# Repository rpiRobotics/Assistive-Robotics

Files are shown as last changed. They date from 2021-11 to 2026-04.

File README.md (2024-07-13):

# Assistive Robotics

This is a repository for multi-robot assitive applications that utilizes Clearpath Dingo Omni-directional robots.

# Computers in the System:

| Description                     | Username      | Hostname (Computer Name) | MAC Address       | IP            | Password  | OS           | ROS     |
| ------------------------------- | ------------- | ------------------------ | ----------------- | ------------- | --------- | ------------ | ------- |
| GUI Tablet                      | tablet        | tablet20                 | AC:67:5D:57:30:50 | 192.168.1.99  | 1234      | Ubuntu 20.04 | Noetic  |
| Main Computer                   | ???           | ?????                    | 3C:8C:F8:EB:0E:C8 | 192.168.1.100 | ????      | Ubuntu 20.04 | Noetic  |
| Dingo 1 Base (Right Arm Config) | administrator | cpr-do100-10000050       | 0C:7A:15:CB:A6:0B | 192.168.1.101 | clearpath | Ubuntu 20.04 | Noetic  |
| Dingo 1 Helper                  | oarbot_blue   | oarbot-blue-P15          | F4:46:37:FF:E5:A1 | 192.168.1.102 | 1234      | Ubuntu 18.04 | Melodic |
| Dingo 2 Base (Left Arm Config)  | administrator | cpr-do100-10000051       | F0:B6:1E:B7:29:1F | 192.168.1.103 | clearpath | Ubuntu 20.04 | Noetic  |
| Dingo 2 Helper                  | oarbot_silver | oarbot-silver-P15        | 4C:77:CB:EC:81:87 | 192.168.1.104 | 1234      | Ubuntu 18.04 | Melodic |
| Overhead Camera Kinect Processor| nuc           | nuc-18                   | 1C:69:7A:0D:A3:E0 | 192.168.1.90  | 1234      | Ubuntu 18.04 | Melodic |

# Setting up the system

<details> 
    <summary>Click to expand</summary>

<!-- Simply run
```
./all_devices_initial_setup.bash
``` -->

</details>

<!-- --------------------------------------------------------------------------- -->

# Setting up the Helper Computers

<details> 
    <summary>Installing Ubuntu 18.04 to Lenovo Thinkpad P15 Gen2 Laptops</summary>

## Installing Ubuntu 18.04 to Lenovo Thinkpad P15 Gen2 Laptops

See the hardware specs of this computer model in https://psref.lenovo.com/syspool/Sys/PDF/ThinkPad/ThinkPad_P15_Gen_2/ThinkPad_P15_Gen_2_Spec.pdf

We have
CPU: Core i7-11850H
GPU: NVIDIA T1200 (4GB GDDR4, 60W)
RAM: 16 GB DDR4-3200MHz
SCREEN: 1080P IPS
STORAGE: 512GB SSD M.2 2280 SSD PCIe NVMe
WIFI: Intel Wi-Fi® 6E AX210, 802.11ax 2x2 Wi-Fi + Bluetooth 5.2

### Prepare the BIOS settings

As described here: https://download.lenovo.com/pccbbs/mobiles_pdf/tp_p1_gen2_ubuntu_18.04_lts_installation_v1.0.pdf
(Note that this file is for P1, not for P15, so not all of steps here works for installing ubuntu 18.04 to P15)

- Disable "OS Optimized Defaults" in "Restart"
- Make sure "Hybrid Graphics" is selected instead of "Discrete Graphics" under Config>Display settings. Later we will have to make this "Discrete Graphics" again.
- F10 "Save & Exit"

### Install Ubuntu 18.04 with a USB

- Insert Ubuntu 18.04 installation USB and boot up the laptop.
- Press "Enter" while you are booting.
- Press "F12" to select the USB device.
- In the GRUB menu select "Install Ubuntu"
- Make sure you are connected to internet via Ethernet (WIFI does not work for now)
- Select Normal installation,
- For the Other options select "Download Updates while installing Ubuntu" and "Install third-party software for graphics and Wifi hardware..." options
- Do the storage managements as you wish (I did without encryption)
- For the username and computer name use the devices info table at the top of this readme file.
- After the installation if the computer does not boot after the GRUB menu, (see https://askubuntu.com/questions/162075/my-computer-boots-to-a-black-screen-what-options-do-i-have-to-fix-it.)
- Basically you will boot with nomodeset option  in the grub menu instead of quiet splash and then you will install graphics card after you boot in
- While booting keep pressing "shift" buttons to see GRUB menu,
- Press "e" while the OS that you would like to boot is selected.
- Go to line that starts with "linux" and erase "quiet splash" and write "nomodeset" instead.
- Press "Ctrl+x", you will be able to boot
- We will have to install NVIDIA graphics card and WIFI drivers

### Install NVIDIA drivers

- open a terminal and do `sudo apt update` and `sudo apt upgrade`
- press windows key and search for "Software & Updates"
- From ubuntu Software tab select Download From Main Server
- From Updates tab Select Never for Notify me of a new Ubuntu version
- From Additional Drivers tab select Using Nvidia driver metapackage from nvidia-driver495 (proprietary)
- Press Apply Changes button and once it finished reboot
- This will install the NVIDIA driver but you can also see options of the section 5 of [this](https://download.lenovo.com/pccbbs/mobiles_pdf/tp_p1_gen2_ubuntu_18.04_lts_installation_v1.0.pdf) for other installation options (We did not try those)
- When it boots up, go to BIOS settings and select "Discrete Graphics" instead of "Hybrid Graphics" under Config>Display settings.
- Save and Exit
- Once you reboot, now without doing the "nomodeset" step in GRUB menu you will be able to login

### Install Wifi Drivers

At the time of this installation, the most up-to-date Ubuntu 18.04 kernel version is 5.4.0 (you can check yours with command `uname -a`). However, the wifi hardware used on this computer (Intel Wi-Fi® 6E AX210) requires at least kernel version 5.10 (You can verify this at [here](https://wireless.wiki.kernel.org/en/users/drivers/iwlwifi)).
As stated in one of the answers in [this link](https://ubuntu.forumming.com/question/14149/ubuntu-20-04-lts-driver-intel-wi-fi-6e-ax210-160mhz), "The Linux 5.10 kernel (or later) will ship as part of Ubuntu 21.04 in April. This version will also get backported to Ubuntu 20.04 LTS at a later date. It's possible to manually install a mainline kernel in Ubuntu however if it breaks you get the pieces." We will install kernel 5.11 to make the wifi adapter work, but as suggested in the same answer be warned to review the implications of installing a kernel version manually [here](https://askubuntu.com/questions/119080/how-to-update-kernel-to-the-latest-mainline-version-without-any-distro-upgrade/885165#885165).

#### Installing Kernel 5.11

- First install Mainline as a graphical kernel installing tool. (See details [here](https://ubuntuhandbook.org/index.php/2020/08/mainline-install-latest-kernel-ubuntu-linux-mint/))
- run `sudo add-apt-repository ppa:cappelikan/ppa`
- `sudo apt update`
- `sudo apt install mainline`
- Open Mainline Kernel Installer and install 5.11.0
- After installation, reboot.
- `sudo update-grub` and `sudo reboot`
- As described [here](https://github.com/spxak1/weywot/blob/main/ax210.md#boot-with-kernel-5101), the output of `sudo dmesg | grep iwl` will show us some errors with the information about which firmware we need to install.
- For example we needed `iwlwifi-ty-a0-gf-a0-39` to `iwlwifi-ty-a0-gf-a0-59`.

#### Installing Firmware

- At the output of dmesg command it is suggested to check https://git.kernel.org/pub/scm/linux/kernel/git/firmware/linux-firmware.git/
- Go this website and download the newest firmware (eg. as of today it was linux-firmware-20211027.tar.gz (sig))
- It takes some time to download, be patient
- Uncompress the file with `tar -zxvf linux-firmware-20211027.tar.gz`
- `cd linux-firmware-20211027/`
- Copy the firmwares to `/lib/firmware/` with command `sudo cp -ax * /lib/firmware`
- Now reboot and the wifi should work!

### Additional settings

- Connect the wifi to lab network.
- Open settings on Privacy tab, disable automatic screen lock, location services enabled.
- Sharing tab, enable sharing and screen sharing, select require a password and make the password `1234`
- Power tab, disable dim screen when inactive, blank screen 5 minutes, Automatic suspend OFF, When power button is pressed Power Off
- Details tab, Users tab, Unlock and enable automatic log in
- Install GNOME Tweaks and launch
- On Power tab disable suspend when laptop lid is closed
- Install Dconf Editor and launch
- on /org/gnome/desktop/remote-access, disable require-encryption
- `sudo apt install ssh`

### Install ROS Melodic

- See [here](http://wiki.ros.org/Installation/Ubuntu)

</details>

<details> 
    <summary>Setting Up Kinect Azure</summary>

## Setting Up Kinect Azure

Setup the Sensor SDK and Body SDK for Kinect Azure following https://docs.microsoft.com/en-us/azure/kinect-dk/sensor-sdk-download and https://docs.microsoft.com/en-us/azure/kinect-dk/body-sdk-download .

At the time of this document the support is only for Ubuntu 18.04 with an AMD64 architecture CPU, additionally a dedicated GPU is a must (with minimum model specified as NVIDIA Geforce GTX 1050 see [here](https://docs.microsoft.com/en-us/azure/kinect-dk/system-requirements) for other requirements)

The steps are summarized as:

### Ssh into the Kinect Processor Computer of the robots

The passwords are given at the top for the  Kinect Processors. Use the information given and ssh into the robots. For example,

```
ssh oarbot_blue@192.168.1.101
```

or

```
ssh oarbot_silver@192.168.1.102
```

Then on each robot, follow the steps below:

### Setting up Linux Software Repository for Microsoft Products

```
curl -sSL https://packages.microsoft.com/keys/microsoft.asc | sudo apt-key add -
sudo apt-add-repository https://packages.microsoft.com/ubuntu/18.04/prod
sudo apt-get update
```

### Setting up the SDKs

```
sudo apt install libk4a1.4-dev
sudo apt install libk4abt1.1-dev
sudo apt install k4a-tools
```

### Adding permissions for Azure Kinect as a usb device

```
cd /etc/udev/rules.d
sudo wget https://github.com/microsoft/Azure-Kinect-Sensor-SDK/blob/develop/scripts/99-k4a.rules
```

Plug in the USB of Kinect Azure and connect it to the power. Then you can verify the installation with `k4aviewer` or `k4abt_simple_3d_viewer` commands.

### Setting up the ROS packages for Kinect Azure

(See the instructions for building [here](https://github.com/microsoft/Azure_Kinect_ROS_Driver/blob/melodic/docs/building.md) as reference)

```
sudo apt-get install ros-melodic-rgbd-launch
cd ~/catkin_ws_assistive/src
git clone https://github.com/burakaksoy/Azure_Kinect_ROS_Driver.git
cd ..
catkin_make -DCATKIN_WHITELIST_PACKAGES='azure_kinect_ros_driver'
source ~/.bashrc
source ~/catkin_ws_assistive/devel/setup.bash
```

#### Troubleshooting:
    
If you see this kind of error during the `catkin_make` command execution:

```
    Finding K4A SDK binaries
    CMake Error at Azure_Kinect_ROS_Driver/cmake/Findk4a.cmake:22 (message):
    Error: Azure Kinect SDK Version numbers contain exactly 3 components
    (major.minor.rev).  Requested number of components: 2
    Call Stack (most recent call first):
    /usr/local/share/cmake-3.18/Modules/CMakeFindDependencyMacro.cmake:47 (find_package)
    /usr/lib/cmake/k4abt/k4abtConfig.cmake:3 (find_dependency)
    Azure_Kinect_ROS_Driver/cmake/Findk4abt.cmake:35 (find_package)
    Azure_Kinect_ROS_Driver/CMakeLists.txt:94 (find_package)

    -- Configuring incomplete, errors occurred!
```

Change 2 components in the version number given in this line of file `/usr/lib/cmake/k4abt/k4abtConfig.cmake` from this:

```
find_dependency(k4a 1.3 REQUIRED)
```

to this:
```
find_dependency(k4a 1.3.0 REQUIRED)
```
and try again the `catkin_make` command above. 

*For more information about this issue see: [https://github.com/microsoft/Azure_Kinect_ROS_Driver/issues/143](https://github.com/microsoft/Azure_Kinect_ROS_Driver/issues/143)*

### Adjusting Default launch parameters for Azure Kinect

You can edit the default FPS argument value to 30 in `/src/Azure_Kinect_ROS_Driver/launch/kinect_rgbd.launch`.

Finally you can verify Kinect Ros installation working by

```
roslaunch azure_kinect_ros_driver kinect_rgbd.launch
```

and in a new terminal you can check for the published images with

```
rqt_image_view
```

For further information about the topics and the usage see https://github.com/microsoft/Azure_Kinect_ROS_Driver/blob/melodic/docs/usage.md

### Bonus: Installing Kinect Azure on Ubuntu 20.04
(Source: https://github.com/microsoft/Azure-Kinect-Sensor-SDK/issues/1263#issuecomment-1705808614)

```
sudo apt purge libk4a*
sudo apt purge k4a
sudo apt purge k4a*
sudo apt autoremove 
sudo apt remove libk4a*
sudo apt remove libk4abt*
sudo apt remove libk4a1*
curl -sSL https://packages.microsoft.com/keys/microsoft.asc | sudo tee /etc/apt/trusted.gpg.d/microsoft.asc
sudo apt-add-repository https://packages.microsoft.com/ubuntu/20.04/prod
sudo apt-get update
curl -sSL https://packages.microsoft.com/keys/microsoft.asc | sudo tee /etc/apt/trusted.gpg.d/microsoft.asc
sudo apt-add-repository https://packages.microsoft.com/ubuntu/20.04/prod
curl -sSL https://packages.microsoft.com/keys/microsoft.asc | sudo apt-key add -
sudo apt-add-repository https://packages.microsoft.com/ubuntu/18.04/prod
curl -sSL https://packages.microsoft.com/config/ubuntu/18.04/prod.list | sudo tee /etc/apt/sources.list.d/microsoft-prod.list
curl -sSL https://packages.microsoft.com/keys/microsoft.asc | sudo apt-key add -
sudo apt-get update
sudo apt install libk4a1.4=1.4.1
sudo apt install libk4a1.4-dev=1.4.1
sudo apt install libk4abt1.1-dev=1.1.2
sudo apt install k4a-tools=1.4.1
sudo apt install ros-noetic-rgbd-launch

# Copy rules
# sudo cp 99-k4a.rules /etc/udev/rules.d/

# k4aviewer
# k4abt_simple_3d_viewer 
```

Also hold these packages to prevent update:
```
sudo apt-mark hold libk4a1.4
sudo apt-mark hold libk4a1.4-dev
sudo apt-mark hold libk4abt1.1-dev
sudo apt-mark hold k4a-tools
# sudo apt-mark showhold
# sudo apt-mark unhold <package-name>
```

Moreover, in the `cmakelists.txt` file of the kinect ros package you may need to edit:
```
# find_package(k4a 1.4.0 QUIET MODULE REQUIRED)
find_package(k4a 1.3.0 QUIET MODULE REQUIRED)

...

# find_package(k4abt 1.1.0 QUIET MODULE)
find_package(k4abt 1.0.0 QUIET MODULE)
```

### Bonus 2: How to resolve high CPU usage issue with body tracking
(Source: https://github.com/microsoft/Azure-Kinect-Sensor-SDK/issues/1007)
Set openMP environment variable as 
`export OMP_WAIT_POLICY=Passive`
before launching kinect!!!

</details>

<details> 
    <summary>Setting Up Kinova Arm for robots</summary>

## Setting Up Kinova Arm for robots

### Hardware Setup

1. Plugin the powercable and the joystick
2. Connect the USB cable to your laptop
3. Powerup the arm

The green light on the joystick will be flashing for around a minute. After that, there will be two results after you do that

#### Joystick Steady Green light

You are good to go! Please direct to [software setup](#software-setup).

#### Joystick Green Light flashing or Steady Red Light

You need to update the firmware of the arm. If you try to use the ROS package when this situation happens, it'll show connection error.

1. Please follow the instruction in this [webpage](https://github.com/Kinovarobotics/kinova-ros/issues/248).
2. You can find the latest firmware [here](https://www.kinovarobotics.com/en/resources/gen2-technical-resources).
3. You can find the installation files of Development Center, a GUI available with the SDK [here](https://www.kinovarobotics.com/en/resources/gen2-faq) in the first question of "Usage". If the download link is missing, you can find it [here](https://drive.google.com/file/d/1UEQAow0XLcVcPCeQfHK9ERBihOCclkJ9/view) (File name is "`PS 0000 0009_1.5.1.zip`") and the document [here](https://www.kinovarobotics.com/sites/default/files/UG-008_KINOVA_Software_development_kit-User_guide_EN_R02%20%281%29.pdf) or [here](https://drive.google.com/file/d/1y5TByFsF97s4_zh14E-q0YHSlMr5P1qe/view).
4. We only tested the Development Center in win10 while updating the firmware. However, Development Center in both win10 and ubuntu20.04 (using the ubuntu16.04 version in the file) can connected to the arm and control the arm.
5. While rebooting the arm in the updating firmware step, you might want to do some "physical therapy" for the arm (basically move the arms around) and wait a bit before restarting your arm.

### Software Setup

#### Control the arm via Development Center

You can find the installation files of Development Center, a GUI available with the SDK [here](https://www.kinovarobotics.com/en/resources/gen2-faq) in the first question of "Usage". If the download link is missing, you can find it [here](https://drive.google.com/file/d/1UEQAow0XLcVcPCeQfHK9ERBihOCclkJ9/view) and the document [here](https://www.kinovarobotics.com/sites/default/files/UG-008_KINOVA_Software_development_kit-User_guide_EN_R02%20%281%29.pdf).

#### Add Translation offset if you have Bota Rokubi FT sensors installed on Kinova robots

Since the Kinematics change due to the additional hardware with the installed FT sensor, we need to add translation offset to the robot settings. 

- Open up the Development Center from `/opt/JACO-SDK/GUI/DevelopmentCenter`. 
- From `General Settings` enter `0.077` to `z-axis` (the other axes are 0).
- Select the check box that says `Activate Offset`.
- Hit `Save` button.

Note that after reboot of the arm the check box is automatically unchecked. Instead of opening the Development Center each time, on the joystick of the arm one can press 1 button. It lits up the right most blue light on the joystick which indicates the offset is activated. 

#### Control the arm via ROS package

Please direct [here](https://github.com/eric565648/kinova-ros/tree/noetic-devel) for how to launch the arm, perform joint angle and cartetian space control.

#### Put the arm to service mode

- Plug in USB your robot
- Open the `C:\Program Files (x86)\JACO-SDK\RobotConfiguration` or the equivalent path on you system.
- Put the last firmware you upload in your robot in the firmware folder.
- Run `ActivateServiceConfiguration.exe` (it is a console app, see the outputs by running it from a terminal/command line)
  If that works well at  General setting > update at the arm type field you will see JAco v2 6dof Service.

#### To use admittance control

1. Open Development Center GUI, general setting > update
2. Verify that main firmware is updated.
3. Arm type is in service mode (see above).
4. Actuator firmware is updated.
5. Verify that all the torque sensors are functional. (see details below)
6. Do the torque calibration. (see details below)
7. Verify that the gravity vector and the payload correctly defined. (see details below)

##### Steps 1-4 are already done in the above.

##### 5. Verifying all torque sensors are functional

Open the Development Center and go to Monitoring >angular >torque  column

- Push against each joint to apply an external torque to each joint and observe if the value on screen reacts
  accordingly to your action. Push in both direction and the torque should be positive in one direction and
  negative in the opposite one.
- If it does not react as expected, You have a problem with one or more of your torque sensor.
- If it reacts as expected, try step 6.

##### 6. Doing the torque calibration

Calibrate arm torque by reset sensors to zero value.
Get the user Guide. Go at the page 58 and place the robot at the picture position (candle like position)

- Once the arm is in the right position, you have to open the Development Center and go to Advanced settings and press 4 times to the Apply to all button in torque zero menu.
- Try to put the arm in torque mode with torque console, but close the Development Center before opening Torque console.
- If the arm does not switch to torque control try step 7.

##### 7. Verify that the gravity vector and the payload correctly defined.

- Open the Torque Console Interface and set the Gravity vector.
- Then set the payload if you have one.
- When it is done, try to switch to torque mode with the Torque Console Interface

If after all of those step it continue to not work, it may be a hardware issue. That need further investigation

</details>

</details>

<!-- --------------------------------------------------------------------------- -->

# Setting Up Dingo Base Computers

<details> 
    <summary>Getting Started</summary>

## Getting Started

Four Dingo-O robots arrived with a printed document named "Custom Robot Quickstart Guide". We only needed to apply section 3 and section 5 of this document after the batteries are fully charged (both the robot batteries and the PlayStation controller batteries). The texts are in these sections are copied below:

### Section 3: Getting Started

Your system has been configured to allow you to get started immediately after receipt. Follow these instructions to get
moving.

1. Remove the Dingo's side panels and top fairings (yellow), insert the batteries provided (or confirm they are
   inserted), then replace the top fairings and side panels.
2. Turn on the Dingo via the HMI button pad on the rear. Note that the computer may beep when starting up.
3. Press "PS" button on gamepad to turn it on.

### Section 5: Wireless

To set up the wireless communications on your Dingo, you must either first establish a wired Ethernet connection or use the HDMI output and USB keyboard from the robots's computer. If you use the Ethernet option, connect your computer to an Ethernet port on the Dingo's computer by removing the Dingo fairing, and set a
static IP on your computer to `192.168.131.19` (for example). If there are no free ethernet ports you may temporarily disconnect
one of the payloads such as a lidar sensor. SSH into the robot computer with:

```
ssh administrator@192.168.131.1
```

Enter the login password when prompted. Once you have successfully logged in, you can connect the robot's computer to a desired wireless network.

If you use the HDMI and USB keyboard option, when you bootup the robot, the login terminal screen of Ubuntu comes up. Enter in the username and password given at the top of this document and log in.

Once you log in, you can connect your robot to a desired wireless network using Netplan.

Simply create a file called `60-wireless.yaml` inside of the `/etc/netplan folder` on your robot's computer. Copy and paste
the contents below into the file, and make sure to modify the wireless interface, SSID, and password fields.

```txt
network:
    wifis:
    # Replace WIRELESS_INTERFACE with the name of the wireless network device, e.g. wlane or wlp3s0
    # Fill in the SSID_GOES_HERE and PASSWORD_GOES_HERE fields as appropriate. The password may be included
    as plain-text
    # or as a password hash. To generate the hashed password, run
    # echo -n 'WIFI_PASSWORD' | iconv -t UTF-16LE | openssl md4 -binary | xxd -p
    # If you have multiple wireless cards you may include a block for each device.
    # For more options, see https://netplan.io/reference/
    WIRELESS_INTERFACE:
        optional: true
        access-points:
            SSID_GOES HERE:
            password: PASSWORD_GOES_HERE
        dhcp4: true
        dhcp4-overrides:
            send-hostname: true
```

Once you have saved the file, you will then need to apply your new Netplan configuration and bring up your wireless
connection by running:

```bash
sudo netplan apply
```

More advanced networking examples, including configurations for accessing a wifi network requiring WPA Enterprise
credentials, can be found here:
https://netplan.io/examples/

You can verify that your robot is connected to a wireless network by running:

```bash
ip a
```

This will show all active connections and their IP addresses, including your robot's connection to the desired wireless
network, and the IP address assigned to the robot's computer.

</details>

<details> 
    <summary>Disable the WiFi Power Saving</summary>

List the wifi devices with command:
```
iw dev
```

To check the current power management setting of your WiFi interface, use the following command (Assuming the device is `wlp2s0`):
```
iw dev wlp2s0 get power_save
```

To Disable Power Saving Temporarily (Assuming the device is `wlp2s0`):
```
sudo iw dev wlp2s0 set power_save off
```

To Make the disabling permenant, create a Systemd Service:
```
sudo nano /etc/systemd/system/wifi-power-management.service
```

Paste the following:
```
[Unit]
Description=Disable WiFi Power Management
After=network.target

[Service]
Type=oneshot
ExecStart=/sbin/iw dev wlp2s0 set power_save off
RemainAfterExit=yes

[Install]
WantedBy=multi-user.target
```

Make sure to replace `wlp2s0` with the actual name of your wireless interface.

To enable and start the service:
```
sudo systemctl enable wifi-power-management.service
sudo systemctl start wifi-power-management.service
```

To verify (Assuming the device is `wlp2s0`):
```
iw dev wlp2s0 get power_save
```

**Note:** I also tried installing `NetworkManager` and edit its config file `sudo nano /etc/NetworkManager/conf.d/default-wifi-powersave-on.conf` by making 
```
[connection]
wifi.powersave = 2
```
and then `sudo systemctl restart NetworkManager`. 
However this did not disable the WiFi power management when I tried to verify with `iw dev wlp2s0 get power_save` command. Therefore I selected to use creating Systemd Service. 

</details>

<details> 
    <summary>Needed Software Customizations on a factory fresh Dingo-O robot</summary>

## Needed Software Customizations on a factory fresh Dingo-O robot

**WARNING: You may want to create a backup of the edited files before begin the process described here.**
To make the dingo robots work as desired in this repository, there are some customizations needed.

Follow the instructions in `ReadMe.md` file of in `src/dingo_customization/` of this repository.

</details>

<details> 
    <summary>Physical UWB setup</summary>

## Physical UWB setup

### Related websites for the Qorvo (DecaWave) UWB module documents

DW1000 [https://www.qorvo.com/products/p/DW1000#documents](https://www.qorvo.com/products/p/DW1000#documents)

DW1001C [https://www.qorvo.com/products/p/DWM1001C#documents](https://www.qorvo.com/products/p/DWM1001C#documents)

DWM1001-DEV [https://www.qorvo.com/products/p/DWM1001-DEV#documents](https://www.qorvo.com/products/p/DWM1001-DEV#documents)

MDEK1001 [https://www.qorvo.com/products/p/MDEK1001#documents](https://www.qorvo.com/products/p/MDEK1001#documents)

### Download the Android DRTLS phone app

[https://www.qorvo.com/products/p/MDEK1001#documents](https://www.qorvo.com/products/p/MDEK1001#documents)

Download DRTLS App : Android Application APK

### Calibration Script

Used to determine the every module's (tags and anchors) offsets based on [this white paper with name: Antenna Delay Calibration of DW1000-Based Products and Systems (Application Note APS014)](https://www.qorvo.com/products/d/da008449).

Set 4 of them an on a nice square with best possible known manual position measurements.

(3 of them gives only one solution, 4 of them gives a Least Squares solution with RMSE error to have an idea of how accurate the calculated offsets are.)

Take note of the manually measured distances, they are needed in the calibration script.

From the android app, put all the modules in the same network and set them as anchors. From the powered ones, only one of them must be set as initiator.

Use `antenna_offset_finding.m` MATLAB script in `uwb_matlab_scripts/` directory of this repo to find the offsets of each UWB module. Then set the offsets in `antenna_calibration.yaml` in `src/assistive_launch/config/` folder. Comments of the script should be sufficient to guide you for further details.

Note: This script would work on Windows 10 but not in Windows 11 as of writing this document. See details [here](https://www.mathworks.com/matlabcentral/answers/1912280-bluetooth-scanning-error-in-windows-11-solutions#answer_1173820)

This script uses the BLE interface of the firmware to communicate with the tags. For further information see section 7 of [DWM1001 Firmware API Guide](https://www.qorvo.com/products/d/da007975)

After the calibration is done, set modules back as tags those you won't to use as anchors from the Android app.

### Script to Calculate and Write the Anchor positions into the Modules

Mount the UWB anchors in the physical workspace area. Measure the distances between them with a laser distance meter.
Use `truck_bay_uwb_locations.m`  MATLAB script in `uwb_matlab_scripts/` directory of this repo. Comments of the script should be sufficient to guide you for further details.

Note: This script would work on Windows 10 but not in Windows 11 as of writing this document. See details [here](https://www.mathworks.com/matlabcentral/answers/1912280-bluetooth-scanning-error-in-windows-11-solutions#answer_1173820)

This script uses the BLE interface of the firmware to communicate with the tags. For further information see section 7 of [DWM1001 Firmware API Guide](https://www.qorvo.com/products/d/da007975)

### Configuring USB Ports of the UWB Tags Mounted on the Robots

At each robot equipped with the UWB tags, this step is required to read data from the UWB tags. 

Determine the USB serial ports of the UWB tags by unplugging and re-pluggin the USB cables of the tags and using this command:

```
ls /dev/serial/by-path/
```

The determined port should be something like this:

```
/dev/serial/by-path/pci-0000:00:14.0-usb-0:3:1.0
```

For each UWB tag, edit the `<robot_name>_uwb_<# of the UWB tag>.yaml` config files in `assistive_launch/config/` directory and assign the `serial_port` parameter to the determined port. 

For example, we name the first Dingo robot as `d1` and the USB port of its `2`nd UWB tag is specified in `assistive_launch/config/d1_uwb_2.yaml` file with the following content:

```
serial_port: '/dev/serial/by-path/pci-0000:00:14.0-usb-0:3:1.0'
topic_name: 'uwb/tag_2_serial_ranging'
```

</details>

<!-- --------------------------------------------------------------------------- -->

# Setting Up Tablet (Graphical User Interface Device) Computer

The tablet device as the GUI of the system is based on 'ARM Smart Teacpendant Project' hardware.

<details> 
    <summary>Tablet OS Setup</summary>

## Tablet OS Setup

### Steps to install Ubuntu (20.04 or 18.04) on Surface Go 2 Tablet

Requires a USB-C to USB-A adapter and flash drive

1. Update Windows 10/11 using Settings -> Updates
2. Download and create Ubuntu 20.04 amd64 USB install drive
3. Disable Windows bitlocker and reboot. If it says “waiting to active”, finish activation, then disable: https://www.isunshare.com/windows-10/4-ways-to-remove-or-disable-bitlocker-encryption-on-windows-10.html
4. Shrink the Windows 10 partition using Windows disk manager: https://www.tenforums.com/tutorials/96288-shrink-volume-partition-windows-10-a.html Suggested to shrink by 64000 MB
5. Connect bootable USB drive and reboot using advanced startup options: https://www.digitalcitizen.life/boot-your-windows-10-pc-usb-flash-drive The bootable usb drive may have the title “Linpus Lite”
6. Install Ubuntu as normal
7. Remove the USB drive
8. At this point Ubuntu is installed, but will not boot automatically. Do the advanced startup options again, and select “ubuntu”. This will boot into Ubuntu.
   Follow these instructions in Ubuntu to disable Windows boot: https://www.reddit.com/r/SurfaceLinux/comments/egds33/possible_fix_for_booting_directly_to_grub_on/ Windows can still be booted using Grub menu
   Ubuntu should now boot. The post is copied here for convenience:

   ```
       Possible fix for booting directly to grub on Surface Go
       If you're having trouble getting your Surface Go to boot to grub instead of the Windows Boot Manager, I might have something to try if you're brave: I moved the Microsoft folder in /boot/efi/EFI out of the way (In Ubuntu: sudo mv /boot/efi/EFI/Microsoft /boot/efi/EFI/Microsoft.bak) and now grub is loaded by default. I'd really only recommend this if you:

       Have a Windows USB recovery made and you know it's bootable

       Have your files backed up off the SSD (both Linux and Windows (if you care))

       Feel comfortable screwing around fixing a potentially broken EFI partition

       Aren't the sort of person who blames other people when you break your own computer following instructions you found on the Internet!

       All that said, it works for me on my recently purchased 8GB/128GB Surface Go w/ Ubuntu 19.10. I had already dumped the WIndows partition though, so I never tested whether grub had any issues loading Windows. You may also need to mess around with efibootmgr to fix the boot order, but I'm not sure.
   ```
9. You may also need to disable secure boot. This is achived from the BIOS settings. To enter the BIOS settings, while powering up the tablet, Press and hold the volume-up button on your Surface and at the same time, press and release the power button. When you see the Surface logo, release the volume-up button.
   The UEFI menu will display within a few seconds.
10. The default kernel version installed with ubuntu 20.04 as of writing this document is 5.15 however this version causes hanging problem when shutting down. Installing kernel version 5.4.243 via Mainline kernel installer resolves the issue for this specific tablet.
11. After the install of the OS, make sure the wifi power saving is disabled by editing:

    ```bash
    sudo nano /etc/NetworkManager/conf.d/default-wifi-powersave-on.conf
    ```

    By default there is:

    ```txt
    [connection]
    wifi.powersave = 3
    ```

    **Change the value to 2**. Then to take effect, run:

    ```bash
    sudo systemctl restart NetworkManager
    ```

    Disabling wifi power saving reduces the wifi latency by a considerable amount! For more information see [here](https://gist.github.com/jcberthon/ea8cfe278998968ba7c5a95344bc8b55).

    ### For further reducing latency, you can tune the network stack with the following commands:

    ```
    sudo sysctl -a | grep ipv4
    sudo sysctl -w net.ipv6.conf.all.disable_ipv6=1
    sudo sysctl -w net.ipv6.conf.default.disable_ipv6=1
    sudo sysctl -w net.ipv6.conf.lo.disable_ipv6=1
    sudo sysctl -w net.core.rmem_default=10000000
    sudo sysctl -w net.core.wmem_default=10000000
    sudo sysctl -w net.core.rmem_max=16777216
    sudo sysctl -w net.core.wmem_max=16777216
    sudo sysctl -w net.ipv4.tcp_low_latency=1  # intended to give preference to low latency over higher throughput; setting =1  # disables IPV4 tcp prequeue processing
    sudo sysctl -w net.ipv4.tcp_timestamps=0  # Only advised in cases where sack is needed.
    sudo sysctl -w net.ipv4.tcp_sack=0  # setting to 1 enables selective acknowledgment for IPV4, which requires enabling tcp_timestamps and adds some packet overhead, which you don't need if you don't experience packetloss
    sudo sysctl -w net.ipv4.tcp_window_scaling=1  # RFC 1323 - support for IPV4 TCP window sizes larger than 64K - generally needed on high bandwidth networks
    sudo sysctl -w net.ipv4.tcp_reordering=3  # The maximum times an IPV4 packet can be reordered in a TCP packet stream without TCP assuming packet loss and going into slow start.
    sudo sysctl -w net.ipv4.tcp_fastopen=1  # Enable to send data in the opening SYN packet.

    sudo sysctl -p # to apply the changes without rebooting

    sudo systemctl restart NetworkManager
    ```

    Note that these changes are not persistent and will be lost after a reboot. To make them persistent, you can add them to the `/etc/sysctl.conf` file as follows:

    ```
    sudo nano /etc/sysctl.conf
    ```

    Paste the following:
    ```
    net.ipv6.conf.all.disable_ipv6 = 1
    net.ipv6.conf.default.disable_ipv6 = 1
    net.ipv6.conf.lo.disable_ipv6 = 1
    net.core.rmem_default = 10000000
    net.core.wmem_default = 10000000
    net.core.rmem_max = 16777216
    net.core.wmem_max = 16777216
    net.ipv4.tcp_low_latency = 1  # intended to give preference to low latency over higher throughput; setting =1  # disables IPV4 tcp prequeue processing
    net.ipv4.tcp_timestamps = 0  # Only advised in cases where sack is needed.
    net.ipv4.tcp_sack = 0  # setting to 1 enables selective acknowledgment for IPV4, which requires enabling tcp_timestamps and adds some packet overhead, which you don't need if you don't experience packetloss
    net.ipv4.tcp_window_scaling = 1  # RFC 1323 - support for IPV4 TCP window sizes larger than 64K - generally needed on high bandwidth networks
    net.ipv4.tcp_reordering = 3  # The maximum times an IPV4 packet can be reordered in a TCP packet stream without TCP assuming packet loss and going into slow start.
    net.ipv4.tcp_fastopen = 1  # Enable to send data in the opening SYN packet.
    ```

    After adding the changes to the `/etc/sysctl.conf` file, you can apply them by running the following command:

    ```
    sudo sysctl -p # to apply the changes without rebooting

    sudo systemctl restart NetworkManager
    ```

    or you can reboot the machine to apply the changes.

    For more information on tuning the network stack, you can refer to the following resources:
    - [https://serverfault.com/q/623780/1102034] (https://serverfault.com/q/623780/1102034)
    - [https://www.speedguide.net/articles/linux-tweaking-121] (https://www.speedguide.net/articles/linux-tweaking-121)
    - [https://itsfoss.com/speed-up-slow-wifi-connection-ubuntu/] (https://itsfoss.com/speed-up-slow-wifi-connection-ubuntu/)

</details>

<!-- --------------------------------------------------------------------------- -->

# System Bootup Process Instructions

<details> 
    <summary>Click to expand</summary>

***Warning:** The order in the following instructions are important for successful bootup process. Following the order especially in the Dingo battery powered up components (Dingo base computer, Dingo helper computer, and Kinova arm) is essential, because otherwise Dingo robots may shut down after ~30 seconds, probably as a default protective measurement by Clearpath (Further investigation is needed on this matter).*

1. Make sure that on each Dingo robot, the Kinova arm is switched off, the Dingo helper computer charger is unplugged, and the robot batteries are connected and charged. 
2. Turn on the master/main computer and run `roscore`.
3. Turn on the GUI tablet.
4. Make sure the overhead Kinect camera is plugged in to the power and connected to the Kinect Azure computer. 
5. Turn on the Overhead Camera (Kinect Azure) computer (NUC).
6. Turn on each Dingo robot by using the button on the robot rear. 
7. Wait for the robot computer to complete its boot up process. 

    *This will launch the default robot control nodes, IMU node, UWB localization nodes, and front and rear Lidar sensor nodes*
8. Switch on the Kinova arm on the robots.
9. Plug in the Dingo helper computer charger.
10. Turn on the Dingo helper computer.  
11. Wait for the Dingo helper computer complete its boot up process. 
12. On master computer, launch `` file. 

     *This launch file will remotely launch
    the GUI node on the GUI tablet,
    the overhead camera and ArUco tag detection robot localization related nodes on the Overhead Camera computer (NUC),
    the Kinova arm, FT Sensor, and Kinect cameras on the Kinova arm wrist on each Dingo helper computer.
    Also, in the master/main computer it will launch
    the human body localization fusion.*

    Note that further devices, nodes, and features can be added to each computer without updating the information written in the last explanation above. That paragraph is intended to cover the main idea of system architecture which explains what system component runs on which computer in the system and therefore to create a sense on the System Bootup Process Instructions.

</details>

<!-- --------------------------------------------------------------------------- -->

# Usage

<details> 
    <summary>Click to expand</summary>

run

```
./test_launcher_all_oarbots.bash
```

Then to correct the torque readings on Kinova arms, run:

```
./correct_kinova_torques.bash
```

To plot the Force/Torque plots either run:

```
./rqt_plotter.bash
```

Or if you have PlotJuggler installed, run:

```
./plotjuggler.bash
```

</details>

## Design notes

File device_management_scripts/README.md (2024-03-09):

# Device Management Scripts

## Overview
``device_management_scripts`` directory contains scripts for managing a network of devices, particularly focusing on tasks like initial setup, git pulling, rebooting, cleaning ROS logs, shutting down, and managing ROS services on Dingo-based robots.

## Scripts Description

### General Device Management Scripts
- `all_devices_git_pull.bash`: Pulls the latest git repository changes onto all devices.
- `all_devices_initial_setup.bash`: Performs the initial setup for all devices.
- `all_devices_reboot.bash`: Reboots all devices.
- `all_devices_rosclean.bash`: Cleans ROS logs on all devices.
- `all_devices_shutdown.bash`: Shuts down all devices.
- `all_devices_terminal.bash`: Opens a new terminal window with tabs for SSH into each device.

### Dingo Robot Specific Scripts
- `all_dingo_bases_restart_ros_service.bash`: Restarts ROS services on all Dingo bases.
- `all_dingo_bases_update_ros_service.bash`: Updates ROS service files on all Dingo bases.

### Configuration Scripts
- Configuration scripts like `dingo_bases.sh`, `dingo_helpers.sh`, etc., define settings for different devices.

### Git Pull Scripts
- Specific scripts for performing git pull operations on different types of devices.

### Initial Setup Scripts
- Scripts for performing initial setup on various devices.

## Usage
To use these scripts:
1. Navigate to the `device_management_scripts` directory.
2. Run the desired script. For example:
   ```bash
   ./all_devices_reboot.bash
   ```

## Notes
- Customize the configuration scripts in the computers directory as per your network setup.
- The scripts are designed for password-based SSH authentication.

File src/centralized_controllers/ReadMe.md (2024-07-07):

# centralized_controllers (Package)

## auto_disable_ekf_localization (Node)

A simple python node, which utilizes the `toggleFilterProcessing`* service of the sensor fusion ([robot_localization](https://github.com/cra-ros-pkg/robot_localization) package ekf) node.  The node will listen for the body joint pose topics coming from the tf body joint broadcaster. Each time a body pose arrives it updates the last time.**
In a separate thread check for how much time has passed since the last message arrival time. If the time passed is more than a timeout (specified as a parameter by the user) call the toggle Filter Processing Node to pause the filter processing while still publishing the last pose. Keep the state of the filter in this node's scope with a private boolean parameter. If the pose messages start coming back, and if we had disabled the filter processing, request to enable it back with the toggle service again. For both toggling operations make sure the request is successful. otherwise do not change the private boolean parameter that holds the filter state and try again in the next iteration of the timer. 

AutoDisabler

*`ToggleFilterProcessingSrv` service allows another node to toggle on/off filter processing while still publishing and Uses a robot_localization package's custom ToggleFilterProcessing service. ([see here for more](https://docs.ros.org/en/noetic/api/robot_localization/html/api/classRobotLocalization_1_1RosFilter.html#ad87227f3976d25577258b1c2cbf8c17a))

**To make the node more general, we will make this node to automatically find all the
`nav_msgs/Odometry`
`geometry_msgs/PoseWithCovarianceStamped`
`geometry_msgs/TwistWithCovarianceStamped`
`sensor_msgs/Imu`
topics that the localization node subscribes to. These are the ROS message types that the `robot_localization` package supports as input ([source](https://docs.ros.org/en/noetic/api/robot_localization/html/preparing_sensor_data.html#adherence-to-ros-standards)). We will create a subscriber for each of them as well and within each subsriber we will simply just update the last arrival time. That's all we need.

Usage of the ToggleFilterProcessingSrv
From a terminal this  DISABLES the processing:
```
rosservice call /human_localization_ekf_se/toggle "'on': false" 
and returns
status: True
```
This ENABLES the processing:
```
rosservice call /human_localization_ekf_se/toggle "'on': false" 
and again returns
status: True
```
if the request is successful.

The definition file of the service has title: `ToggleFilterProcessing.srv`
with the following content:
```
bool on
---
bool status
```

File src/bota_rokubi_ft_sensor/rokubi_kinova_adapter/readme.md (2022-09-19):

# rokubi_kinova_adapter
This is a package for URDF descriptions and mesh files Force torque sensor rokubi mini serial from Bota systems with a custom mechanical Kinova adapter.

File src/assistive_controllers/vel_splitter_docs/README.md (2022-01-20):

# Velocity Splitter

## Goal

The node takes in the desired **end-effector** velocity (with respect to the **world** and **see/represent in the arm base frame (for linear velocity) and in the end-effector frame (for angular velocity)**), and split it into the **arm cartesial velocity**, support height velocity, and the base velocity.

## How to run

```
rosrun assistive_controller vel_splitter.py
```

If you would like to use the kinematic simulation with rviz, do
```
roslaunch oarbot_description oarbot_rviz.launch
```

You can pose the robot to the home pose in the simulation with the command.
```
rosservice call /go_home
```

## Input Output

### Subscribe

#### Desired End-Effector Velocity

- Topic: desired_vel (geometry_msgs::Twist)
- Description: The desired velocity of the end-effector **with respect to the world** and **represent in the arm base frame/the support frame (for linear velocity) and in the end-effector frame (for angular velocity)**. Please note that which frame the velocity is represent in is very important. 

#### Joint State

- Topic: /joint_state (sensor_msgs::JointState)
- Description: The joint state of the Oarbot. Oarbot is a 10 Dof robot. The 10 axises are *linear x*, *linear y*, *angular z*, *support height in z* and the 6 axis of Kinova arm. In the real set up, *linear x*, *linear y*, *angular z* is the (2D) estimated location (localization) of the Oarbot with respect the world (a map frame you defined).

### Publish

#### Arm Cartesian Velocity

- Topic: arm_cartesian_vel (kinova_msgs::JointVelocity)
- Description: The arm cartesian velocity represent **in the base frame for linear velocity** and **in the end-effector frame for angular velocity**. You can map this topic directly to the cartesian velocity topic of kinova arm.

#### Support Height Velocity

- Topic: sup_vel (std_msgs::Float64)
- Description: 1 DoF support height velocity.

#### Base Velocity

- Topic: cmd_vel (geometry_msgs::Twist)
- Description: The base cartesian velocity represent **in the base footprint frame** (like all mobile robots would defined, e.g. Husky from Clearpath). You can map this topic directly to the car command topic of the base.

## How it works?

The underlying mechanic behind the velocity splitter is using quadratic programming with weighting based on the distance of the end-effector to a pre-defined point. The following descirbed the flow of the node.

### Transform the velocity to the arm base frame
The node first transform the velocity (the angular velocity in particular) to the arm base frame so that all velocity are represented in the same frame.

### Estimate Joint Velocity using Quadratic Programming

QP_eqn

The QP try to optimized the above equation. You can see that as the weighting get higher, the respected joint velocity will be lower which then it will decide to use the arm more or the base more.

Since the velocity are represented in the arm base frame, the Jacobian matrix is actually a (J_T)arm_base which means it's the Jacobian matrix of the end-effector represented in the arm base frame. 

### Convert Joint Velocity to Cartisian Velocity

We can then use arm jacobian matrix to convert the joint velocity to the arm cartesian velocity, and also converted the angular velocity to represent in the end-effector frame. The support height velocity is simply the joint velocity. The base velocity is also converted to the base footprint frame.

## Performance Example

The is the result of moving in y direction, i.e. the desired velocity is has a linear y component, from the distance of the end effector to the predefined constrained center ~0.01 m. One can see that the arm velocity approach to 0 as the end-effector goes to the surface of the sphere (the pre-defined constrained distance).

rvsvel
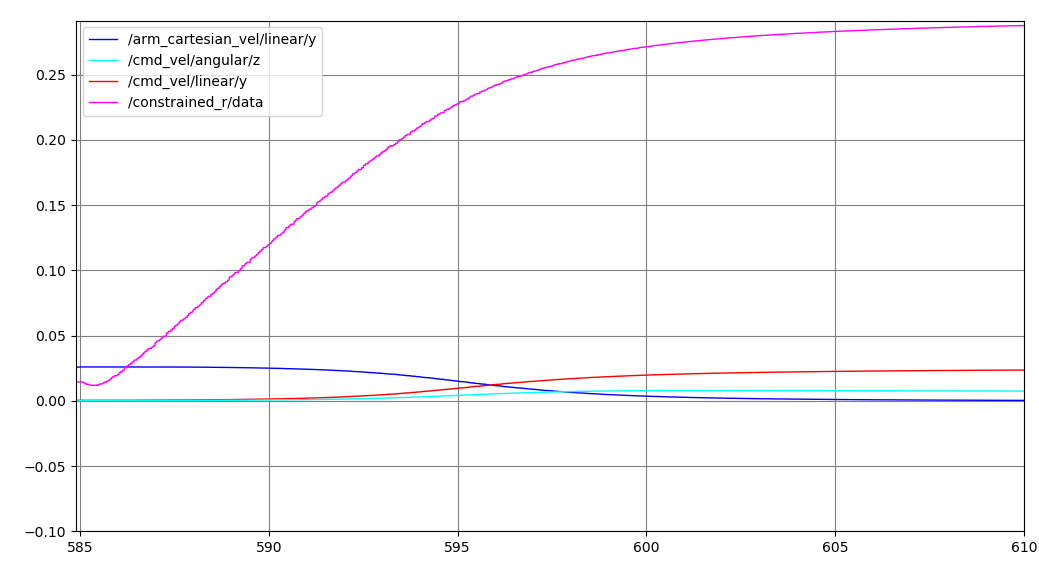
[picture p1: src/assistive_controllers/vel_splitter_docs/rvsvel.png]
rvsvel


You can see that there's a angular velocity in base. This is because the angular velocity can also cause y-direction linear velocity represented in the arm base frame.

## Debug Hints

1. The constrained sphere center (in the arm base frame) and distance can be adjust in line 80 81.
```
self.control_center = np.array([0.5,0,0.3])
self.control_r = 0.33
```

2. Make sure that the joint state match between how the code realized and the actual robot state. Otherwise different joint state may cause mis calculation of Jacobian matrix and the contrained status.

3. Map the velocities (the arm velocity, the base velocity and support height velocity) to the right topic.

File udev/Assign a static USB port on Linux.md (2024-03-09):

Source: [https://msadowski.github.io/linux-static-port/](https://msadowski.github.io/linux-static-port/)

Assign a static USB port on Linux
=================================

Quite often I found myself needing static device names in Linux, especially when using _ROS_. As an example imagine having two sensors of a same type that yo connect to your PC. Now, if you don’t map your ports in any way you might end up with devices being mapped to _/dev/ttyACM0_ and _/dev/ttyACM1_, depending which one was connected first.

Let’s say your sensors are at different positions on the robot. If you want to make sure that you are using the proper device in your code you can either:

1.  Unplug and plug back the sensors again until you get the names you want
2.  Assign a static name to a port and be done with it

If you want to learn about the option 2 then read on.

_Otherwise keep playing with your cables!_

Follow the .rules
=================

Below I will show you the steps to create a symbolic link for the USB device so that you don’t have to replug anything ever again to fix the order of the devices.

*   List USB attributes for the device:

`udevadm info --name=/dev/ttyACMx --attribute-walk`

Where _x_ is a number matching your device port. In the attribute list you should look for an attribute that is unique for a device (check _idVendor_ and _idProduct_).

*   Create (or open) a file `_/etc/udev/rules.d/99-usb-serial.rules_`
*   If you found an unique attribute of the device then write a following line in the rules file:

`KERNEL=="ttyACM*", ATTRS{idVendor}=="6472", SYMLINK+="sensor_0"`

If there is nothing unique in the two of your sensors, you can do static assignment based on the USB kernel (so basically whatever device you connect to a given port it will create a symbolic link with a same name). It works well even with USB hubs!

`KERNEL=="ttyACM*", KERNELS=="1-4:1.0", SYMLINK+="sensor_0"`

*   Reload your udevadm rules:

`udevadm control --reload-rules`

Now, if everything went correctly you can connect your device and type in your terminal:

`ls /dev/sens*`

to see if you successfully created a symlink. Since it’s a symbolic link you will be able to access both _/dev/sensor\_0_ and _/dev/ttyACM0_ but they will point to the same device.

That’s it, now (hopefully) you don’t have to reconnect your sensor every time you are running your ROS nodes.

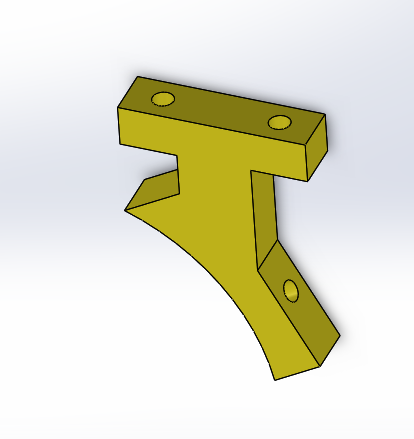
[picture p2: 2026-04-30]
hardwares/wrist_connection.PNG

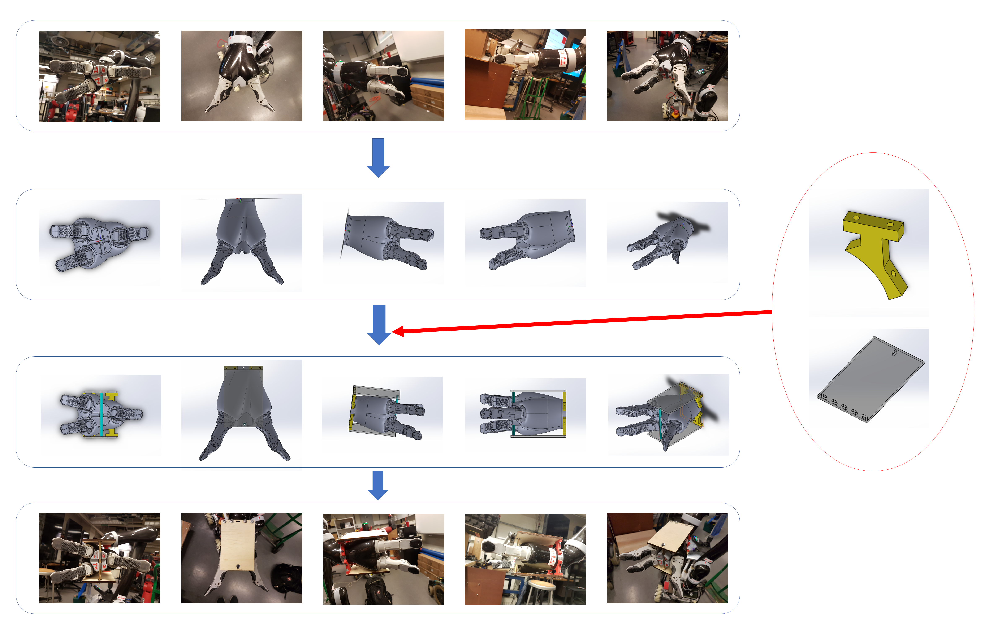
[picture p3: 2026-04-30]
hardwares/Cam-holder-design.png

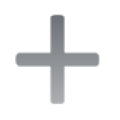
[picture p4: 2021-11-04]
src/assistive_gui/resource/+.PNG

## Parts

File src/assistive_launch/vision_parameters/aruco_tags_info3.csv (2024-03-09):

place | aruco_type | id | size_mm | x | y | z
floor | DICT_5X5_50 | 0 | 190 | 0 | 3.664 | 0
floor | DICT_5X5_50 | 1 | 190 | 0 | 0 | 0
floor | DICT_5X5_50 | 2 | 190 | 8.122 | 0 | 0
floor | DICT_5X5_50 | 3 | 190 | 8.122 | 3.664 | 0
floor | DICT_5X5_50 | 4 | 190 | 0 | 1.832 | 0
floor | DICT_5X5_50 | 5 | 190 | 4.061 | 0 | 0
floor | DICT_5X5_50 | 6 | 190 | 8.122 | 1.832 | 0
floor | DICT_5X5_50 | 7 | 190 | 4.061 | 3.664 | 0
floor | DICT_5X5_50 | 8 | 190 | 0 | 0.916 | 0
floor | DICT_5X5_50 | 9 | 190 | 3.04575 | 0 | 0
floor | DICT_5X5_50 | 10 | 190 | 7.10675 | 0 | 0
floor | DICT_5X5_50 | 11 | 190 | 8.122 | 2.748 | 0
floor | DICT_5X5_50 | 12 | 190 | 5.07625 | 3.664 | 0
floor | DICT_5X5_50 | 13 | 190 | 1.015 | 3.664 | 0
floor | DICT_5X5_50 | 14 | 190 | 0 | 2.748 | 0
floor | DICT_5X5_50 | 15 | 190 | 1.015 | 0 | 0
floor | DICT_5X5_50 | 16 | 190 | 5.07625 | 0 | 0
floor | DICT_5X5_50 | 17 | 190 | 8.122 | 0.916 | 0
floor | DICT_5X5_50 | 18 | 190 | 7.10675 | 3.664 | 0
floor | DICT_5X5_50 | 19 | 190 | 3.04575 | 3.664 | 0
floor | DICT_5X5_50 | 20 | 190 | 2.035 | 3.664 | 0
floor | DICT_5X5_50 | 21 | 190 | 2.035 | 0 | 0
floor | DICT_5X5_50 | 22 | 190 | 6.0915 | 0 | 0
floor | DICT_5X5_50 | 23 | 190 | 6.0915 | 3.664 | 0
floor | DICT_5X5_50 | 24 | 190 | 3.04575 | 3.664 | 0
floor | DICT_5X5_50 | 25 | 190 | 2.035 | 3.664 | 0
floor | DICT_5X5_50 | 26 | 190 | 2.035 | 0 | 0
floor | DICT_5X5_50 | 27 | 190 | 6.0915 | 0 | 0
floor | DICT_5X5_50 | 28 | 190 | 6.0915 | 3.664 | 0
oarbot_blue | DICT_4X4_50 | 2 | 360 | -0.228 | -0.003 | 0.845
oarbot_silver | DICT_4X4_50 | 1 | 360 | -0.233 | 0 | 0.855
d1 | DICT_4X4_50 | 0 | 360 | -0.25 | 0 | 0.50635
d2 | DICT_4X4_50 | 4 | 360 | -0.25 | 0 | 0.50635

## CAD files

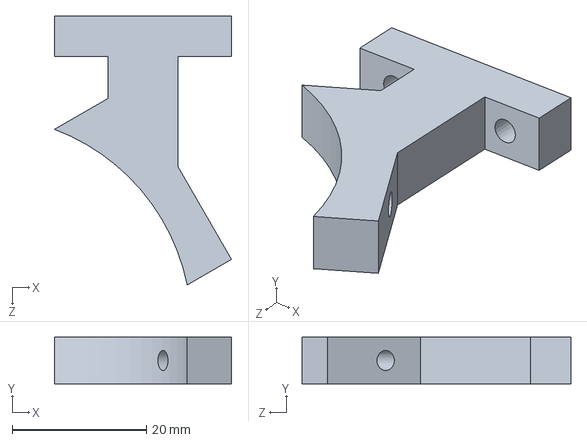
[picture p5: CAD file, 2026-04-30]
hardwares/wrist_connection.SLDPRT
26.4 x 7.00 x 40.1 mm

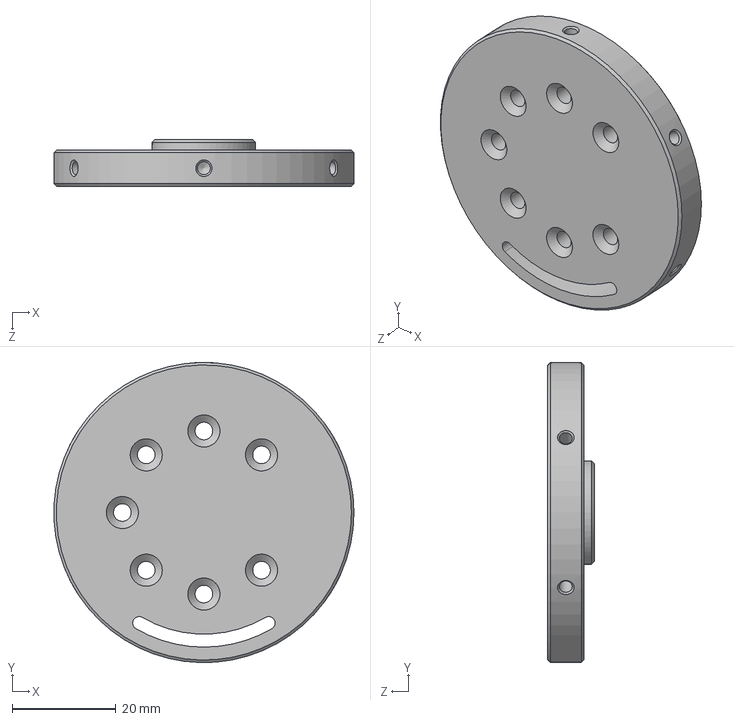
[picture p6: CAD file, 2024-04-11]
src/bota_rokubi_ft_sensor/rokubi_kinova_adapter/docs/RokubiFTSensorAdapterKitGripperCADs/ACC-KINOVA-ROK-ROK-P012_CONFIG-Default_REV-A.step
58.0 x 58.0 x 9.00 mm

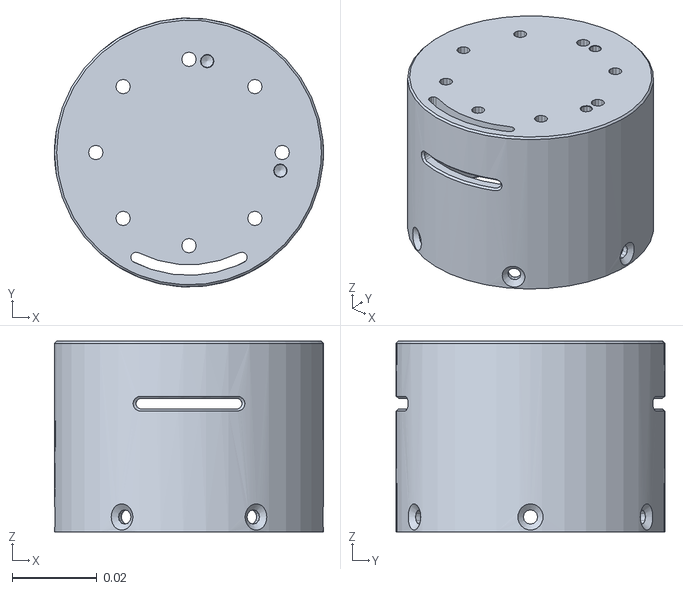
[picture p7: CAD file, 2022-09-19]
src/bota_rokubi_ft_sensor/rokubi_kinova_adapter/meshes/adapter/mounting.STL
0.0635 x 0.0634 x 0.045

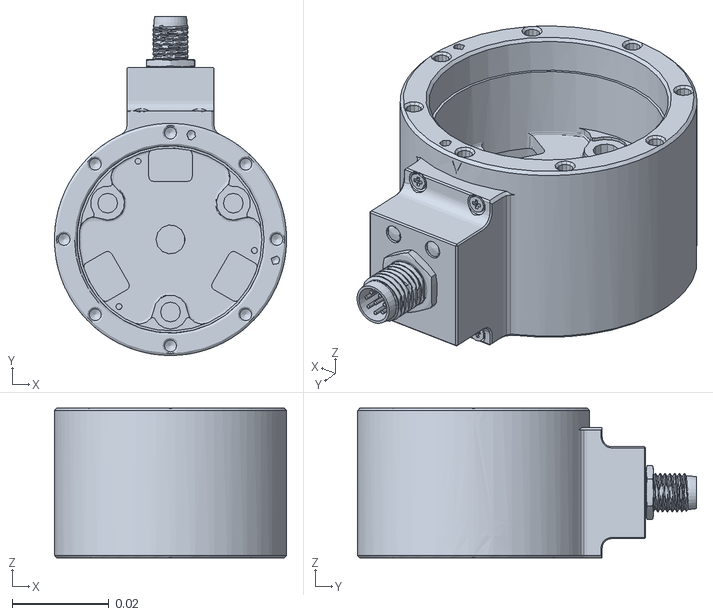
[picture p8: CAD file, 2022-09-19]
src/bota_rokubi_ft_sensor/rokubi_kinova_adapter/meshes/sensor/BFT_ROKS_SER_M8/mounting.STL
0.048 x 0.0701 x 0.031

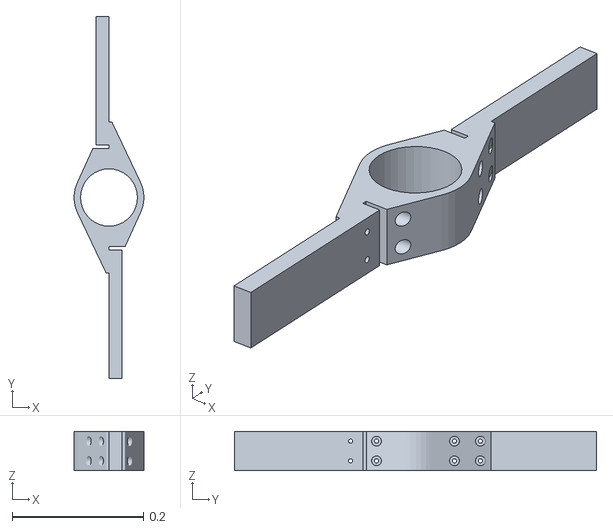
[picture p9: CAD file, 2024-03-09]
src/dingo_customization/meshes/pvc_riser_uwb_mount.STL
0.107 x 0.552 x 0.06

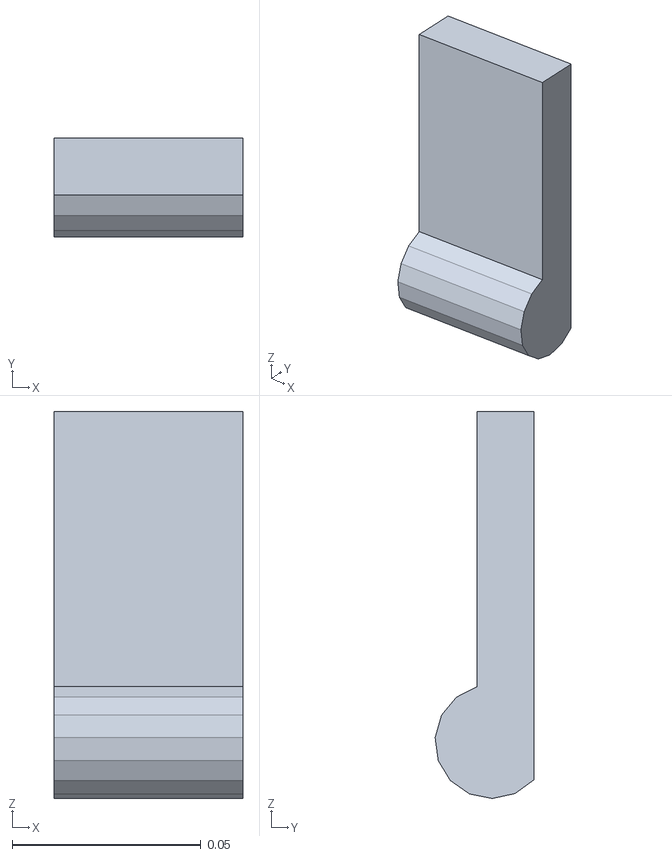
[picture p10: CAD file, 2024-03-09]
src/uwb_reader/meshes/Decawave.stl
0.05 x 0.0261 x 0.102

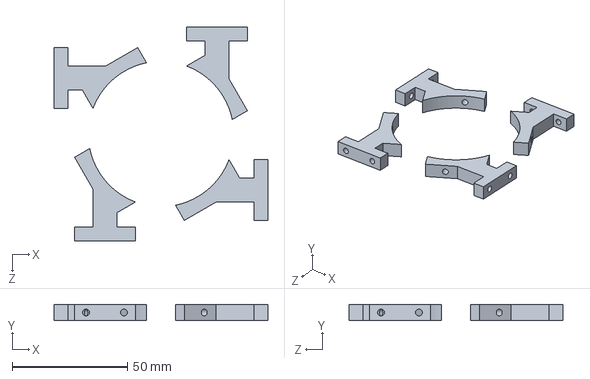
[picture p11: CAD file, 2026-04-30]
hardwares/wrist_connection_multiple.SLDPRT
92.8 x 7.00 x 92.8 mm

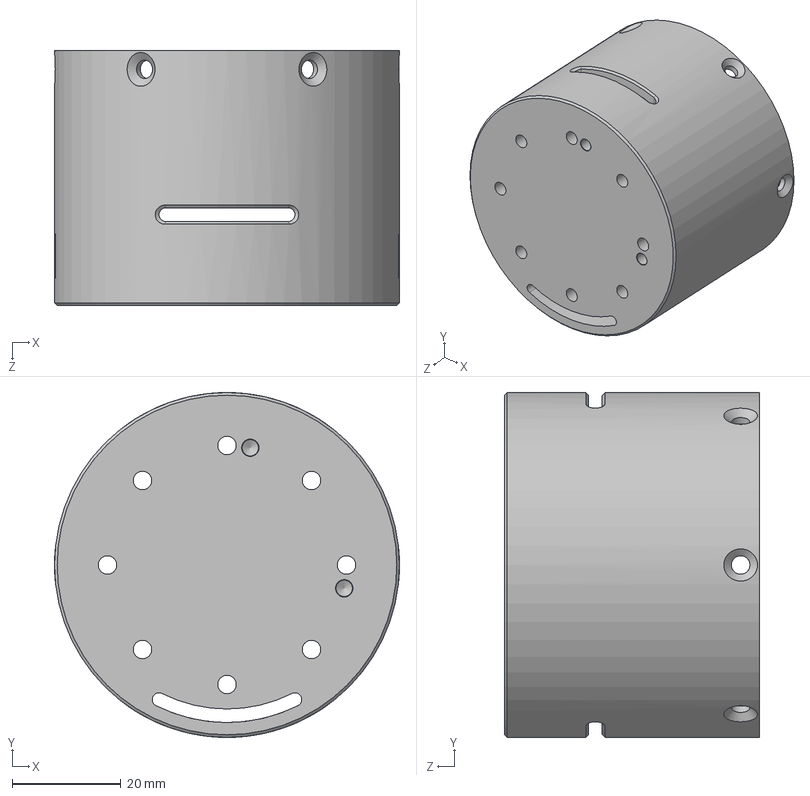
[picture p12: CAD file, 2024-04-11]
src/bota_rokubi_ft_sensor/rokubi_kinova_adapter/docs/RokubiFTSensorAdapterKitGripperCADs/ACC-KINOVA-ROK-ROK-P011_CONFIG-Default_REV-A.step
63.5 x 63.5 x 47.0 mm

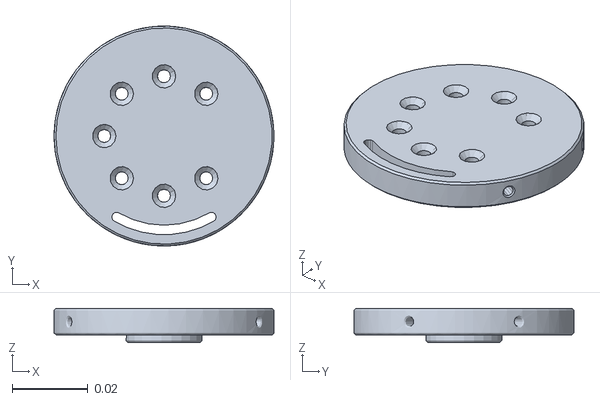
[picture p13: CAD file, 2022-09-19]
src/bota_rokubi_ft_sensor/rokubi_kinova_adapter/meshes/adapter/gripper_adapter.STL
0.058 x 0.058 x 0.009

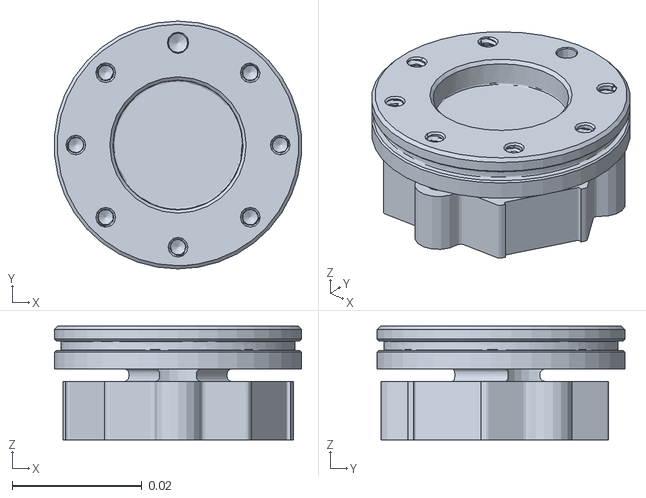
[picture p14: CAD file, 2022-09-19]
src/bota_rokubi_ft_sensor/rokubi_kinova_adapter/meshes/sensor/BFT_ROKS_SER_M8/wrench.STL
0.0381 x 0.0382 x 0.0175

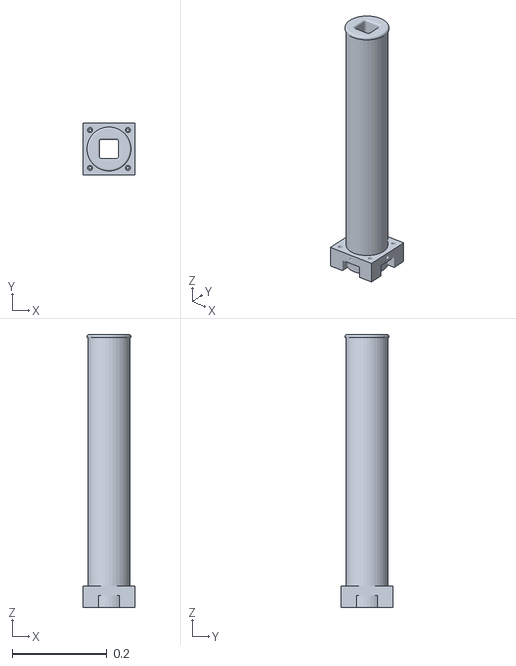
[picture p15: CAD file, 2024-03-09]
src/dingo_customization/meshes/pvc_riser.STL
0.11 x 0.11 x 0.576

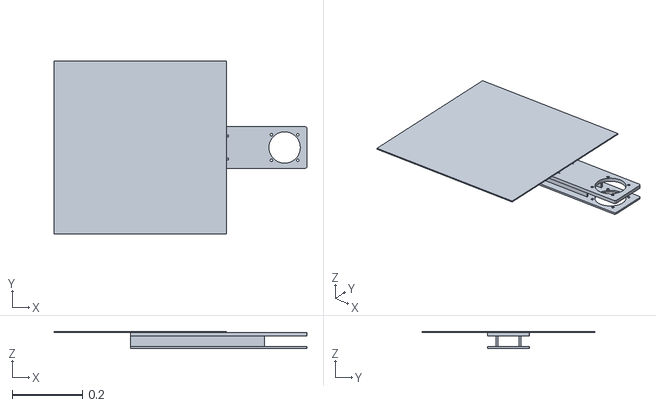
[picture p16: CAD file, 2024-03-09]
src/dingo_customization/meshes/pvc_riser_aruco_mount.STL
0.718 x 0.49 x 0.0484

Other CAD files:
hardwares/wrist_connection.STL
hardwares/wrist_connection_multiple.STL

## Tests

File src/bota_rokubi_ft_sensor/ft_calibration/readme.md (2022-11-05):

# FT calibration scripts
```
python ft_calibration.py
```
Reads csv file with joint values of kinova arm for the calibration orientations of the FT sensor. Jogs the robot to those poses one by one. At each point, Subscribes to the IMU messages and Wrench msgs reads them 100 times, takes the average (Note that from IMU, only the accelerations are needed, however they need to be on the same frame with wrench, so make sure they are published in the same frame, eg use a IMU transformer). After the averaging data is collected for that point with a matrix. After the all data is collected, a least squares estimate is used to estimate the sensor offsets (Fx,Fy,Fz,Tx,Ty,Tz) end effector mass(m) and center of mass coordintes in wrench frame (cx, cy, cz) is calculated and printed to the terminal as, for example: 

```
calib_residuals: [361.85667464]
mass: 1.2271697966535375
COM_pos: [ 0.0407208  -0.00243385  0.05250709]
F_bias: [-1.56365157 -3.58940157 -1.63655572]
T_bias: [ 0.06126408 -0.03329708 -0.1085475 ]
Calibration process ended successfully. You need to save these values to your ft calib data / gravity compensation parameter file..
```

For OARbots these parameters are needed to be saved to yaml files named `oarbot_blue_ft_calib_data.yaml` and `oarbot_silver_ft_calib_data.yaml` . This yaml file later can be used with a gravity compansation node to remove the static errors on the FT sensor. Oarbot launchers handles such compensation already but at every launch one also needs to call the bias calibration service with:
```
rosservice call /oarbot_blue/imu_gravity_compensation/calibrate_bias
rosservice call /oarbot_silver/imu_gravity_compensation/calibrate_bias
```

### Unknowns: 
- Bias (6x1), Gripper mass(scalar), CoM (3x1)
### Method:
- Create a csv file of robot poses at different orientations
- Jog robot to each pose one by one
- Use IMU data from Kinect for gravity vector
- Transform IMU to wrench frame
- Collect FT and IMU data at each pose.
- Create measurement matrix and vector based on Newton-Euler (static)
- After all poses visited apply Least Squares Estimation (LSE) for the unknowns

#### Newton-Euler (static)
$$
\begin{aligned}
&F_m^{(3 \times 1)}=-m g^{(3 \times 1)}+F_{\text {bias }}^{(3 \times 1)} \\
&T_m^{(3 \times 1)}=g^{\times} m c^{(3 \times 1)}+T_{\text {bias }}^{3 \times 1}
\end{aligned}
$$

#### Newton-Euler in matrix form to structure for LSE 
$$
Z = Hx
$$

where; 

$$
Z=\left[\begin{array}{l}
F_m^{(3 \times 1)} \\
T_m^{(3 \times 1)}
\end{array}\right]^{6 \times 1},
$$

$$
H=\left[\begin{array}{cccccccccc}
-g_x & 0 & 0 & 0 & 1 & 0 & 0 & 0 & 0 & 0 \\
-g_y & 0 & 0 & 0 & 0 & 1 & 0 & 0 & 0 & 0 \\
-g_z & 0 & 0 & 0 & 0 & 0 & 1 & 0 & 0 & 0 \\
0 & 0 & -g_z & g_y & 0 & 0 & 0 & 1 & 0 & 0 \\
0 & g_z & 0 & -g_x & 0 & 0 & 0 & 0 & 1 & 0 \\
0 & -g_y & g_x & 0 & 0 & 0 & 0 & 0 & 0 & 1
\end{array}\right]^{6 \times 10}
$$ 

and,

$$
x=\left[\begin{array}{l}
m \\
m c_x \\
m c_y \\
m c_z \\
F_{\text { bias }}^{(3 \times 1)} \\
T_{\text {bias }}^{(3 \times 1)}
\end{array}\right]^{(10\times 1)}
$$

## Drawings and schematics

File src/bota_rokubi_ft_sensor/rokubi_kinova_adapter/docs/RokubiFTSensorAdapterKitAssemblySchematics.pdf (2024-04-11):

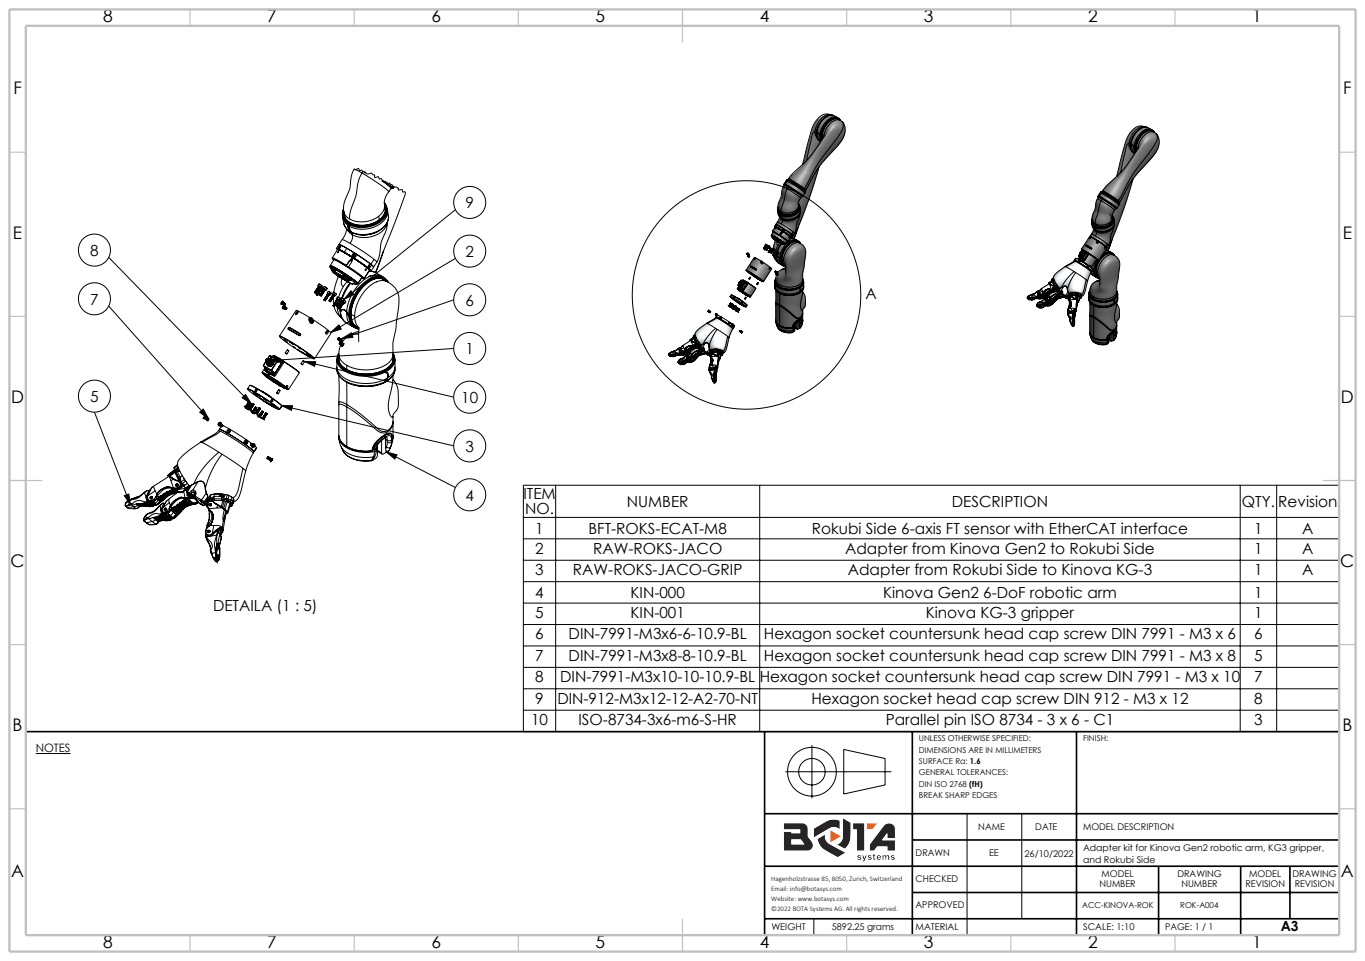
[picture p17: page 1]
DETAILA (1 : 5); DIN-7991-M3x8-8-10.9-BL; Hexagon socket countersunk head cap screw DIN 7991 - M3 x 8

ITEM NO. | NUMBER | DESCRIPTION | QTY. Revision
1 | BFT-ROKS-ECAT-M8 | Rokubi Side 6-axis FT sensor with EtherCAT interface | 1 | A
2 | RAW-ROKS-JACO | Adapter from Kinova Gen2 to Rokubi Side | 1 | A
3 | RAW-ROKS-JACO-GRIP | Adapter from Rokubi Side to Kinova KG-3 | 1 | A
4 | KIN-000 | Kinova Gen2 6-DoF robotic arm | 1
5 | KIN-001 | Kinova KG-3 gripper | 1
6 | DIN-7991-M3x6-6-10.9-BL | Hexagon socket countersunk head cap screw DIN 7991 - M3 x 6 | 6

8 | DIN-7991-M3x10-10-10.9-BL Hexagon socket countersunk head cap screw DIN 7991 - M3 x 10 | | 7
9 | DIN-912-M3x12-12-A2-70-NT | Hexagon socket head cap screw DIN 912 - M3 x 12 | 8
10 | ISO-8734-3x6-m6-S-HR | Parallel pin ISO 8734 - 3 x 6 - C1 | 3

NOTES | | UNLESS OTHERWISE SPECIFIED: DIMENSIONS ARE IN MILLIMETERS SURFACE Ra: 1.6 GENERAL TOLERANCES: DIN ISO 2768 (fH) BREAK SHARP EDGES | FINISH:

NAME | DATE | MODEL DESCRIPTION

DRAWN | EE | 26/10/2022 | Adapter kit for Kinova Gen2 robotic arm, KG3 gripper, and Rokubi Side

Hagenholzstrasse 85, 8050, Zurich, Switzerland Email: info@botasys.com Website: www.botasys.com ©2022 BOTA Systems AG. All rights reserved. | CHECKED | | | MODEL NUMBER | DRAWING NUMBER | MODEL REVISION | DRAWING REVISION

APPROVED | | | ACC-KINOVA-ROK | ROK-A004

WEIGHT | 5892.25 grams | MATERIAL | | SCALE: 1:10 | PAGE: 1 / 1 | A3

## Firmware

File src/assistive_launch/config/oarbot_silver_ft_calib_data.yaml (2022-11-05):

# ns: "" #(string, default: "~") #All published topics are pushed down into the <ns> namespace, i.e., the topics for the compensated force-torque measurements (ft_zeroed and ft_compensated) will be published under <ns> (<ns>/ft_zeroed and <ns>/ft_compensated.

bias: [-1.56365157, -3.58940157, -1.63655572,  0.06126408, -0.03329708, -0.1085475] # 6x1 double array which contains the ([fx, fy, fz, tx, ty, tz]) force-torque bias of the force-torque sensor.

gripper_mass: 1.2271697966535375 # (double) mass of the gripper attached to the force-torque sensor.

gripper_com_frame_id: "j2n6s300_left_wrench" # (string) ID of the frame in which the gripper center of mass is expressed.

gripper_com_child_frame_id: "j2n6s300_left_gripper_com" #(string) ID of the (child) frame of the gripper center of mass. This can be freely chosen by the user.

gripper_com_pose: [ 0.0407208,  -0.00243385,  0.05250709,
  0.0, 0.0, 0.0] # (double array) 6x1 array ([x y z r p y]) with x,y,z translation and roll, pitch, yaw orientation (in meters and radians) containing the pose of the gripper COM expressed in the gripper_com_frame_id frame

gripper_com_broadcast_frequency: 100 # (double, default: 100.0) broadcast frequency (in Hz) of the gripper COM pose on /tf.

loop_rate: 100 # (double, default: 1000.0) frequency (in Hz) of the main loop of the gravity compensation node (should be at the same # frequency as the publish frequency of the force-torque sensor).

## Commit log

2021-11-05 change motor serials
2021-11-05 motor debug
2021-11-12 implement single body joint tf broadcaster
2021-11-17 write a node for tf publishing a body joint from camera
2021-11-17 add yaml and launch files for tf body single joint
2021-11-17 implement tf broadcaster btw end effector and camera base
2021-11-19 Update all devices git pull for kinova and kinect
2021-11-20 update kinova arm feedback rate to 100hz and fix remote kinect launch issue
2021-11-21 implement body single joint follower
2021-11-24 implemnt all body joints tf broadcaster
2021-11-29 test 2 robots 2 joints following
2021-11-30 Add tf prefix for all joints tf publisher to distunguish the source
2021-12-01 Adjust poses btw world frame and kinova arm roots
2021-12-01 try to launch joint followers inside the robots
2021-12-01 try shoulder joints
2021-12-02 Update kinova joint speed limits to max
2021-12-09 set feedback publish rates to 50Hz
2021-12-10 Add payload values for kinect attached
2021-12-13 Increase rate to 100Hz from kinova and kinect
2021-12-14 Increase tf rates to 200Hz for practically obtain 100Hz
2021-12-30 make razer laptop the master device
2021-12-30 make razer laptop the master device 2
2021-12-30 Works successfuly: All Devices Initial Setup New bash
2022-01-12 vel split using qp, linear frame in arm base, angular frame in ee
2022-01-13 add new device NUC for kinect aruco localizations
2022-01-13 add vision parameter files
    [aruco_tags_info3.csv]
2022-01-18 more precise measurements
    [aruco_tags_info3.csv]
2022-01-19 update motor serial ports
2022-01-19 correct motor controller port info
2022-01-23 add qp solvers installations to all devices install script
2022-01-27 try joint follower with redundancy resolver
2022-01-27 adjust joint follower for whole oarbot to follow, not just arm
2022-01-30 Add arm finger control layout to GUI
2022-02-02 joint follower yaml adjustment
2022-02-05 implement new joint follower with admittance control
2022-02-22 implement overhead camera publish PoseWithCovarianceStamped
2022-02-25 measure imu locations on robot
    [aruco_tags_info3.csv]
2022-02-25 add udev rule for microstrain imu device
2022-03-02 enable back joint following flag
2022-03-04 Add body joint following launchers to oarbot launchers
2022-03-09 Add measurements for laser scanner pose
2022-03-09 correct naming to laser_scanner_2d from 2d_laser_scanner
2022-03-09 Add top camera view to rviz
2022-03-10 start integrating laser scanner into obstacle avoidance
2022-03-11 integrate laser scanner into obstacle avoidance
2022-03-11 Consider laser scanner obtacle as a single object
2022-03-29 add parameter for motor control frequency
2022-03-29 increase base control rate 100hz from 25hz - experimental
2022-04-03 Revet- increase base control rate 100hz from 25hz - experimental
2022-05-26 add deadzone for joint torques, disable FT deadzone
2022-05-27 assign joint torque threshold to each joint
2022-08-17 update vision camera parameters (lab relocation)
2022-09-19 create rokubi ft sensor description package
    [gripper_adapter.STL, mounting.STL, wrench.STL]
2022-09-19 Add yaml files for kinova helper publisher & edit for ft sensor
2022-09-19 Summon FT reltd src's in bota_rokubi_ft_sensor dir
    [gripper_adapter.STL, mounting.STL, wrench.STL]
2022-09-20 adjust arm2camera tf for new camera mounting
2022-09-20 add installation of ft sensor to inital setup.bash
2022-09-20 set rights for realtime priority of ft sensor in initial setup.bash
2022-09-20 Add FT sensor launchers and config files
2022-09-20 add udev rule for bota rokubi ft sensor device
2022-09-21 Implement TF broadcasster: Arm to FT sensor
2022-09-21 revert using additional frame, but keep the src code
2022-09-21 start implementing ft calibrator
    [ft_calibration_joint_poses_right.csv, ft_calibration_joint_poses_right2.csv]
2022-09-21 adjust kinect IMU rate to 100Hz
2022-09-21 add imu filter and add it to launchers
2022-09-21 use imu transformer package for ft sensor imu
2022-09-22 add data collection to ft calibratior
2022-09-22 Complete Ft calibrator and Add ft gravity compensation
2022-09-22 re-calibration ft -oarbot_blue
2022-10-02 Update readme of FT calibration scripts
2022-11-05 calibrate ft sensor of oarbot_silver
2024-03-09 initial commit to dingo transition
    [Decawave.stl, aruco_tags_info3.csv, pvc_riser.STL, pvc_riser_aruco_mount.STL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]
2024-03-09 update stl files
    [pvc_riser.STL]
2024-03-09 debug stl files and update dingo xacro
    [pvc_riser.STL, pvc_riser_aruco_mount.STL, pvc_riser_uwb_mount.STL]
2024-03-10 debug for nuc overhead camera
    [aruco_tags_info3_old.csv, aruco_tags_info3_original.csv]
2024-03-16 Resolve error flood in redundancy_resolver.py when arm joint states are not yet published.
2024-03-16 reduce periods of warning in body joint follower
2024-03-16 Separated the launch files of Kinect camera and Kinova arm
2024-04-11 Added Rokubi FT sensor docs
    [ACC-KINOVA-ROK-ROK-P011_CONFIG-Default_REV-A.step, ACC-KINOVA-ROK-ROK-P012_CONFIG-Default_REV-A.step]
2024-06-14 Add service call to reset FT sensor bias when enabling admittance control
2024-06-21 revert back to 25cm control ball radius
2024-06-21 Comment out launching Kinova Helper Publishers. Because they are not used when there is an external FT sensor
2024-07-02 Attempt to resolve issue of Resetting body joint pose does not work properly in body joint follower
2024-07-02 resolved "invalid frame configuration! the values for map_frame, odom_frame, and base_link_frame must be unique." issue
2024-07-04 debug on joint follower pose error
2025-01-18 Try adding direct world frame cmd_vel to the redundancy resolver
2025-02-14 revert back to default home joint angles and control ball configs in redundancy resolution
2025-02-27 revert back to default home joint angles and control ball configs in redundancy resolution p2
2025-09-23 use the existing joint follower as the slave and another script to plan out the target tf
2025-09-24 add swarm following in joint follower code
2025-09-24 get swarm frame name from server while update. and static parameter name
2025-09-25 the desired frame is different
